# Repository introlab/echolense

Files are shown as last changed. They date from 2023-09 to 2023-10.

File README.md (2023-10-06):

<p align="center">
 <picture>
  <source media="(prefers-color-scheme: dark)" srcset=".github/logo_dark_theme.svg" width="520">
  EchoLense
 </picture>
</p>

EchoLense is an open-source acoustic camera made by [IntRoLab](https://introlab.3it.usherbrooke.ca/mediawiki-introlab/index.php/Main_Page). It aims to provide a flexible platform for the scientific community to further research in the field. It can be built with common off-the-shelf components and a 3D printer. This repo contains the STL files to build one as well as assembly instructions. We also provided 1000 room impulse responses (RIRs) that we measured with the device and you'll find python scripts to measure your own too.

## Assembly instructions

### Bill of material

_We are not affiliated with any of the links provided below. Those are just examples of components similar to the ones we used._

<div align="center">

|         **Part**         | **Number** |                                              **URL**                                              |
|:------------------------:|:----------:|:-------------------------------------------------------------------------------------------------:|
|    3D printed housing    |      1     |               _See housing folder of this repo_       |
|    Arducam USB camera    |      1     |               [Link](https://ca.robotshop.com/products/arducam-8mp-1080p-usb-camera-module)      |
| ReSpeaker Mic Array v2.0 |      1     | [Link](https://ca.robotshop.com/products/seeedstudio-respeaker-mic-array-v20-far-field-4-pdm-microphones)|
|       M2x6mm screws      |      5     |                                                 -                                                 |
|       M3x4mm screws      |      2     |                                                 -                                                 |
| Micro USB to DIP adapter |      1     |          [Link](https://www.amazon.ca/Adapter-Female-Connector-Converter-pinboard/dp/B0CDBP341B/)         |
|   4-Wires ribbon cable   |      1     |                                                 -                                                 |

</div>

### Instructions
1. Remove the camera's native USB connector.
2. Cut the ribbon cable so it has a length of around 90 mm and solder one of its ends to the camera's USB pads. Solder the other end of the cable to the micro USB adapter.

   <details>
    <summary><em>Illustration</em></summary>
    <p align="center">
     <picture>
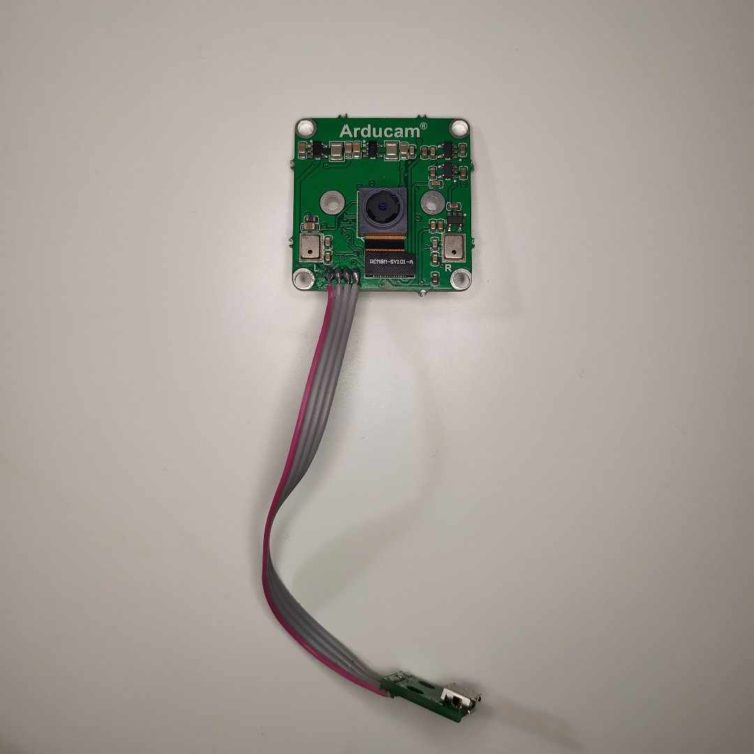
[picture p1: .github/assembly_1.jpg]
      
     </picture>
    </p>
   </details>

4. Using the two M3x4mm screws, secure the micro USB adapter in the bottom half of the housing.

   <details>
    <summary><em>Illustration</em></summary>
    <p align="center">
     <picture>
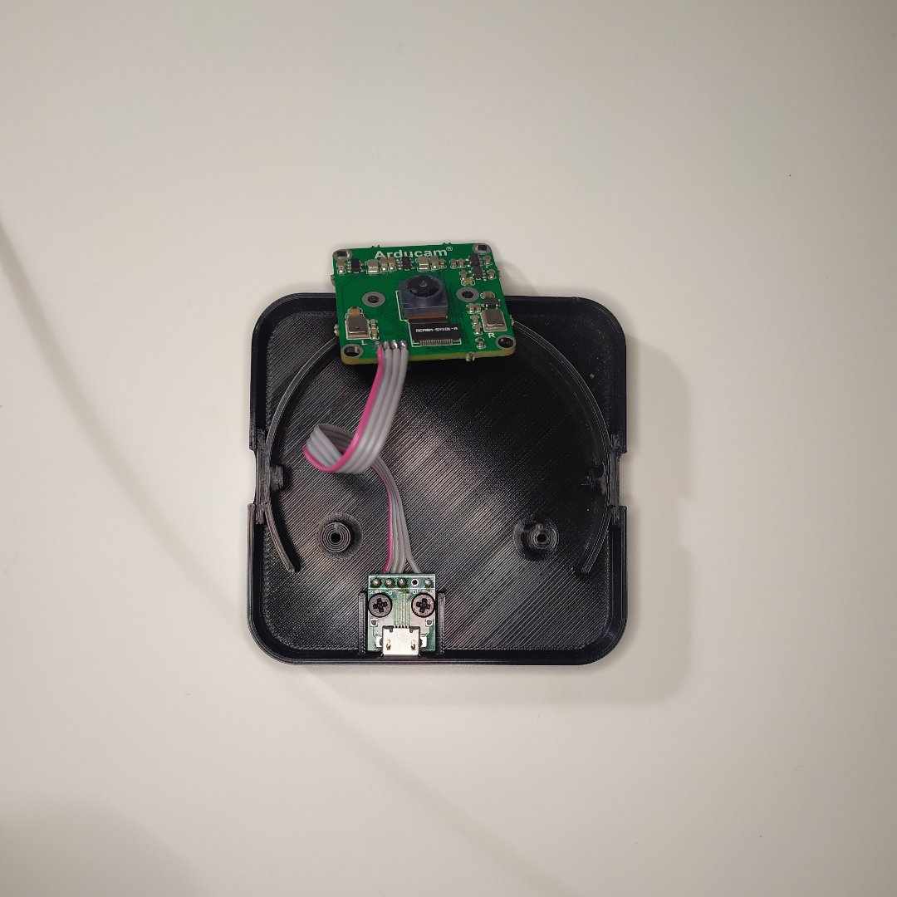
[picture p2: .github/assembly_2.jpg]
      
     </picture>
    </p>
   </details>

6. Insert the camera in its socket.
7. Align the mic array with the holes in the bottom half of the housing, place the camera on top of the mic array and secure everything using three M2x6mm screws.

   <details>
    <summary><em>Illustration</em></summary>
    <p align="center">
     <picture>
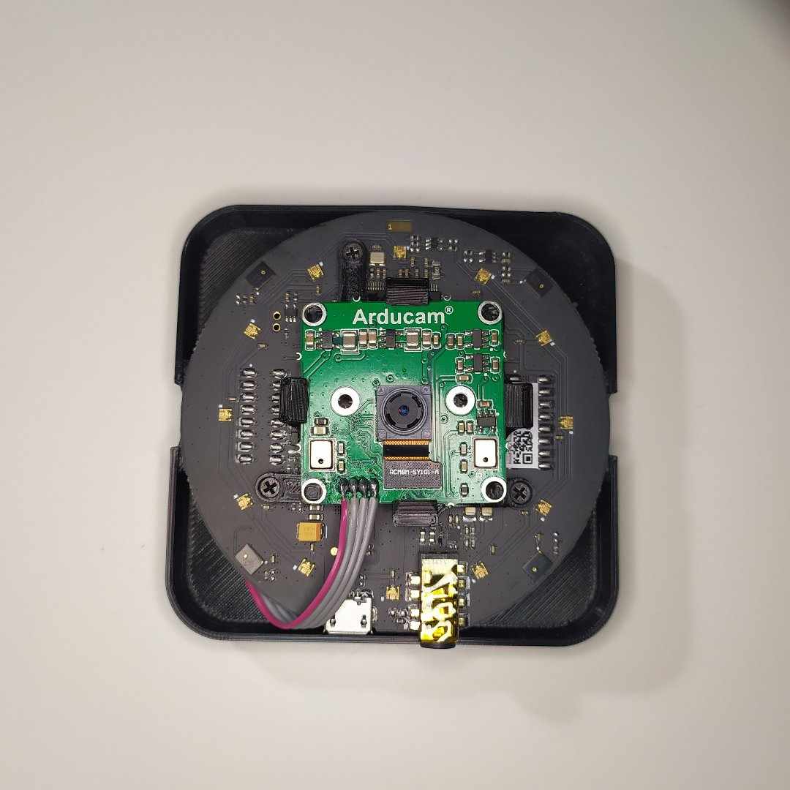
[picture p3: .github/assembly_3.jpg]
      
     </picture>
    </p>
   </details>

8. Close the housing and secure it using the remaining M2x6mm screws and the holes on the sides.

## Room impulse responses

### The "rirs" folder

The RIRs are measured using the technique propose in the following paper:\
[Farina, Angelo. (2000). Simultaneous Measurement of Impulse Response and Distortion With a Swept-Sine Technique](https://www.researchgate.net/publication/2456363_Simultaneous_Measurement_of_Impulse_Response_and_Distortion_With_a_Swept-Sine_Technique) 

In "rirs", you'll find three subfolders...

1. The "recordings" folder contains the exponential sine sweeps (ESS) recordings.
2. The "processings" folder contains the uncut RIRs obtained from the recordings.
3. The "toolkit" folder contains mainly two python scripts. The first one is `record.py`. It is used to produce and record ESSs and save them in the "recordings" folder. The second one is `process_recordings.py` and simply extracts the RIRs from the "recordings" folder and saves them in the "processings" folder.

### Record new ESSs
1. Check the parameters at the top of the `record.py` file to make sure that they fit your needs.
2. Launch the recording script:
```bash
cd rirs
python -m toolkit.record -o <output_dir> # output_dir will be created in the recordings directory
```
3. Start a recording by pressing the space bar on your keyboard. By default, the sound will come out by the active speaker on your computer and be recorded by the mic array.
4. Delete the last recording by pressing the "x" key on your keyboard if you need to.

### Extract RIRs from the recordings
 ```bash
 cd rirs
 python -m toolkit.process_recordings
 ```

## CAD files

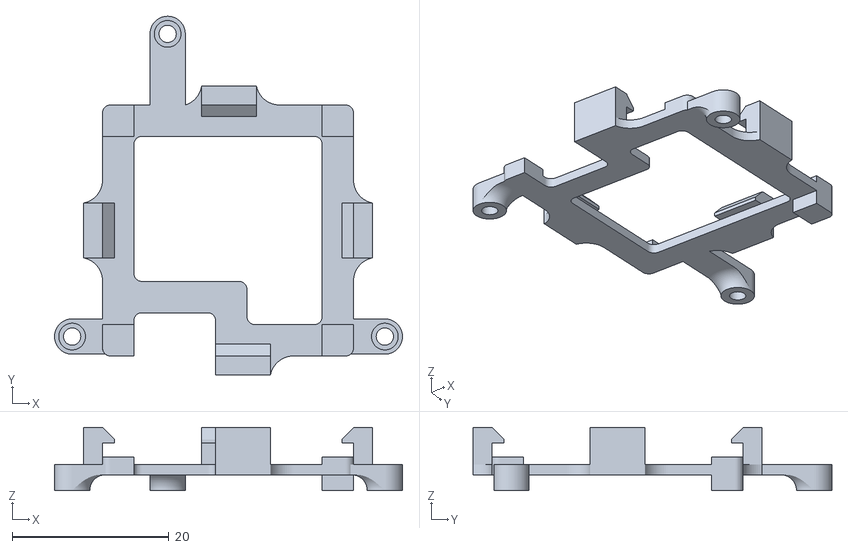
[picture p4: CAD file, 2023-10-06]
housing/camera_socket.stl
44.3 x 45.7 x 8.03

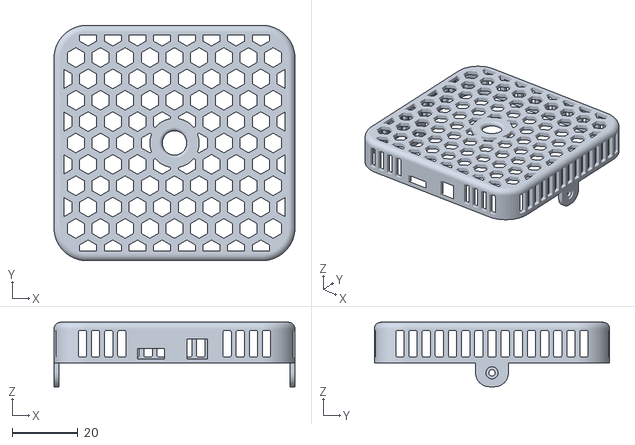
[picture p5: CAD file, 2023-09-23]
housing/upper_housing.stl
73.3 x 71.6 x 19.6

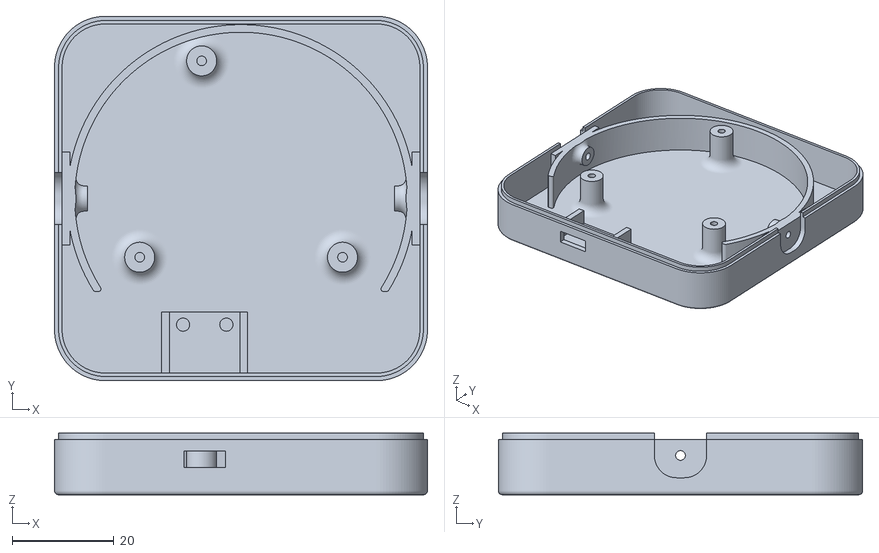
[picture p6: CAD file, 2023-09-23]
housing/lower_housing.stl
73.3 x 71.6 x 12.1

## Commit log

2023-09-24 Housing and RIRs upload
    Author: William Aris <william.aris@usherbrooke.ca>
    [camera_socket.stl, lower_housing.stl, upper_housing.stl]
2023-09-24 Housing and RIRs upload
